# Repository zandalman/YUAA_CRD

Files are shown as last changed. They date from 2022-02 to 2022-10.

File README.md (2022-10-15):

## YUAA CRD

### Purpose
Our goal is to develop a cosmic ray detector (CRD) to serve as the scientific payload for the Yale Undergraduate Aerospace Association (YUAA) CubeSat. We will use cosmic rays to map the boundaries of the South Atlantic Anomaly (SAA).

### General CubeSat Info

CubeSats are miniature satellites composed of units consisting of 10 cm cubes. Yale was chosen by NASA as one of sixteen schools across the country whose CubeSat will be launched into space as auxiliary payloads on NASA missions. The Yale CubeSat consists of two 10 cm cube units. The CubeSat team is divided into several subteams: attitude determination and control (ADCS), radio, software, and cosmic ray detector (CRD). The CRD team interacts significantly with the ADCS and software teams. The software team writes C programs for our I2C components. We work with the ADCS team to coordinate mechanical design in the CubeSat, which is necessary due to the size constraints. The bulkiest part of the ADCS system is the gravity gradient boom (GGB), a measuring tape which spools out of the bottom of the CubeSat to generate restoring torques which stabilize the CubeSat’s orientation. The GGB includes a rotary encoder which provides feedback on the length of the GGB. The ADCS system also includes magnetorquers, electromagnets which generate torques using the Earth’s magnetic field, to maneuver the CubeSat.

### Background

#### Cosmic Rays

Cosmic rays are high-energy radiation originating from outside the solar system. About 99% of cosmic rays are bare atomic nuclei. 90% of these nuclei are protons (hydrogen nuclei), 9% are alpha particles (helium nuclei), and 1% are heavier elements. The other 1% of cosmic rays are beta particles (solitary electrons). Cosmic rays also include trace amounts of antiparticles like positrons and antiprotons. Sometimes, gamma rays (high-energy photons) are also considered cosmic rays. When cosmic rays enter the Earth’s atmosphere, they collide with atoms and molecules, producing a cascade of lighter particles known as secondary cosmic rays. Secondary cosmic rays are typically composed of neutrons, pions, kaons, and their antiparticles. Pions and kaons quickly decay into muons, neutrinos, and their antiparticles, which can be detected on Earth’s surface. The muon lifetime of 2.2 us should not be enough for muons to reach the surface of Earth, but due to relativistic time dilation their effective lifetime is longer in our reference frame. 1 Muons have similar properties to electrons but about 200 times the mass. Because muons are charged particles, we can use muons to test our detection circuitry before sending it into space.

#### Earth’s Magnetic Field

The Earth has a dipolar magnetic field generated by convection currents in Earth’s molten iron and nickel outer core. Energetic charged particles originating from solar wind and cosmic rays are captured by Earth’s magnetic field. Charged particles in a magnetic field move in helices about magnetic field lines. The concentration of charged particles peaks in two distinct regions above Earth’s surface, known as the inner and outer Van Allen belts. The gap between the Van Allen belts is caused by low frequency radio waves whose origin is still an area of active
research. 

There is a nonzero angle between the axis of Earth’s dipole magnetic field and its axis of rotation, causing the inner Van Allen belt to make its closest approach of about 2000 km to Earth’s surface above the South Atlantic. This region of enhanced radiation is called the South Atlantic Anomaly (SAA). The SAA dips low enough to intersect low Earth orbit. Satellites passing through the SAA are exposed to elevated levels of radiation for minutes at a time, leading to malfunctions, loss of observational time for telescopes, and danger to astronauts in the ISS.

#### Scintillators

A scintillator is a material that emits photons when excited by ionizing radiation. Commonly used scintillators often emit photons in the optical bands. There are many types of scintillators including organic crystals, organic liquids, plastic scintillators, inorganic crystals, gaseous scintillators, glasses, and perovskites. We use plastic scintillators, in which the primary fluorescent emitter, or fluor, is suspended in a base.

### Design

#### Mechanical

Using a band saw and a mill, we cut the scintillator down to a 1 cm cube due to size constraints in the CubeSat. Within the SAA, the particle flux is so high that our detection events would overlap. A layer of aluminum shielding around the scintillator reduces the number of events to the order of ~100 events per second. We calculated that a shielding thickness of 7 mm is sufficient. Because protons are more massive than electrons, cosmic ray protons typically have more energy than cosmic ray electrons, so the ratio of proton to electron events increases with shielding thickness.

The shielding is a 25 x 25 x 28 mm rectangular prism of aluminum with an 11 x 11 x 14 mm hole in the center for the scintillator cube and the SiPM. For ease of machining, the shielding is composed of 3 sections which are held together by 6-32 screws. At each of the bottom corners, the aluminum extends slightly further to give space for mounting holes.

When a charged particle passes through the scintillator, it deposits its kinetic energy into photons. We coat five sides of the scintillator with a reflective paint so that most photons eventually exit the scintillator at a single face. The non-coated face has a silicon photomultiplier (SiPM) which will detect the photons. The SiPM is optically coupled to the scintillator with optical jelly, an amorphous material with a prescribed refractive index. The SiPM is held fast against the scintillator by rubber stops which push against the inside faces of the shielding.

The SiPM is soldered onto a small printed circuit board (PCB) using a ball grid array (BGA). The PCB contains pads for the anode and cathode. Wires will be soldered directly to these pads and exit the shielding through a hole. The SiPM is AC coupled to a charge-sensitive preamplifier (preamp). The AC coupling circuit and the preamp come from an evaluation kit created by Ketek. The AC coupling circuit is mounted in a Thorlabs mount and the preamp is mounted in a rectangular aluminum box which acts as a Faraday cage, protecting it from radiation.

All of the circuitry minus the AC coupling circuit and preamp are contained on a custom 4-layer PCB, whose irregular shape is determined by the size constraints imposed by the GGB. This custom PCB will connect to the SiPM, AC coupling circuit, and preamp by a combination of wires and micro coax cables. Wires will be twisted together in pairs for extra stability.

#### Electrical

Our custom analog circuitry will count the number of cosmic ray detection events and classify them according to particle type. Our integrated circuit (IC) components communicate with the onboard computer (OBC) using I2C protocol, which requires clock and data lines. We have access to one set of clock and data lines from the OBC. An important aspect of I2C is that two devices cannot use the same clock and data lines if they have the same I2C address. Most IC chips which use I2C have address pins which allow you to set the I2C address to avoid overlap. We also have access to a 5 V power supply from the OBC.

As charged particles pass through the scintillator, their kinetic energy is converted into photons which activate cells on the SiPM. The SiPM is an avalanche photodiode, meaning that it consists of an array of photodiode cells. When a photon hits a cell, the cell emits electrons via the photoelectric effect. There is some “dead time” where the cell cannot detect another photon, so having an array of cells allows the SiPM to detect many photons in quick succession. The output pulse generated by the SiPM from a detection event is a sum of the signals generated by all of the photons produced by the particle passing through the scintillator.

The SiPM is AC coupled to a charge-sensitive preamp. In contrast to DC coupling, AC coupling rejects DC components of the signal, blocking any DC bias or offset voltage. AC coupling becomes important when the pulse frequency is sufficiently high that pulses overlap, resulting in a nonzero offset.

The preamp creates output pulses with an integrated voltage equal to the integrated current (i.e. charge) of the input pulses. The charge of the input pulses is physically meaningful because it is proportional to the total energy of the photons collected by the SiPM. The output pulses from the pre-amp look like a steep rising edge followed by an exponential decay with a time constant of ~100 ns. The height of the pulses ranges from 10 mV to 100 mV depending on the type of particle. Because all pulses have approximately the same shape, we can use the height of the pulse as a proxy for the integrated voltage. This pulse height analysis (PHA) is common in radiation detection.

If we had a larger budget, we would use a commercial multi-channel analyzer (MCA). However, instead we bin pulses by pulse height manually. Each pulse height bin is created with a system of three high-speed comparators. Two comparators act as upper and lower discriminators and a third comparator acts as an AND gate, only outputting high if the input voltage is between the two discriminators. The comparators are contained in IC chips with 4 comparators each. We have 7 bins total, so we need 21 comparators or 6 IC chips. The discriminator levels are set by 8 bit digital-to-analog converters (DACs). The DACs are contained in an IC chip with 8 DACs.

The outputs from the comparators are fed into real time clock (RTC) IC chips, which we program to count the number of pulses over the course of 5 min. There are 8 RTC chips, 7 for the pulse height bins and one for counting pulses from the rotary encoder for the GGB. The RTC chips only have one I2C address bin and therefore only two possible I2C addresses. We use an I2C multiplexer to mediate communication between the OBC and the RTC chips. The multiplexer has one input set of clock and data lines and four output sets of clock and data lines which each are used by 2 RTC chips, one with each possible I2C address.

We only have access to a 5 V power supply from the OBC. However, the preamp requires a 12 V power supply and the AC coupling circuit requires a 30 V bias voltage. We use boost converters to generate these voltages from the 5 V supply. All components draw negligible current, so there is no worry about drawing too much current.

The light output of the scintillator is temperature dependent and we don’t know exactly what the equilibrium temperature will be in the CubeSat once it is in space. Therefore, we use resistor temperature devices (RTDs) to monitor the temperature on our custom PCB and near the shielding.

The code for interfacing between the OBC and the I2C components of the circuit is managed by
the software subteam of the CubeSat and is available upon request.

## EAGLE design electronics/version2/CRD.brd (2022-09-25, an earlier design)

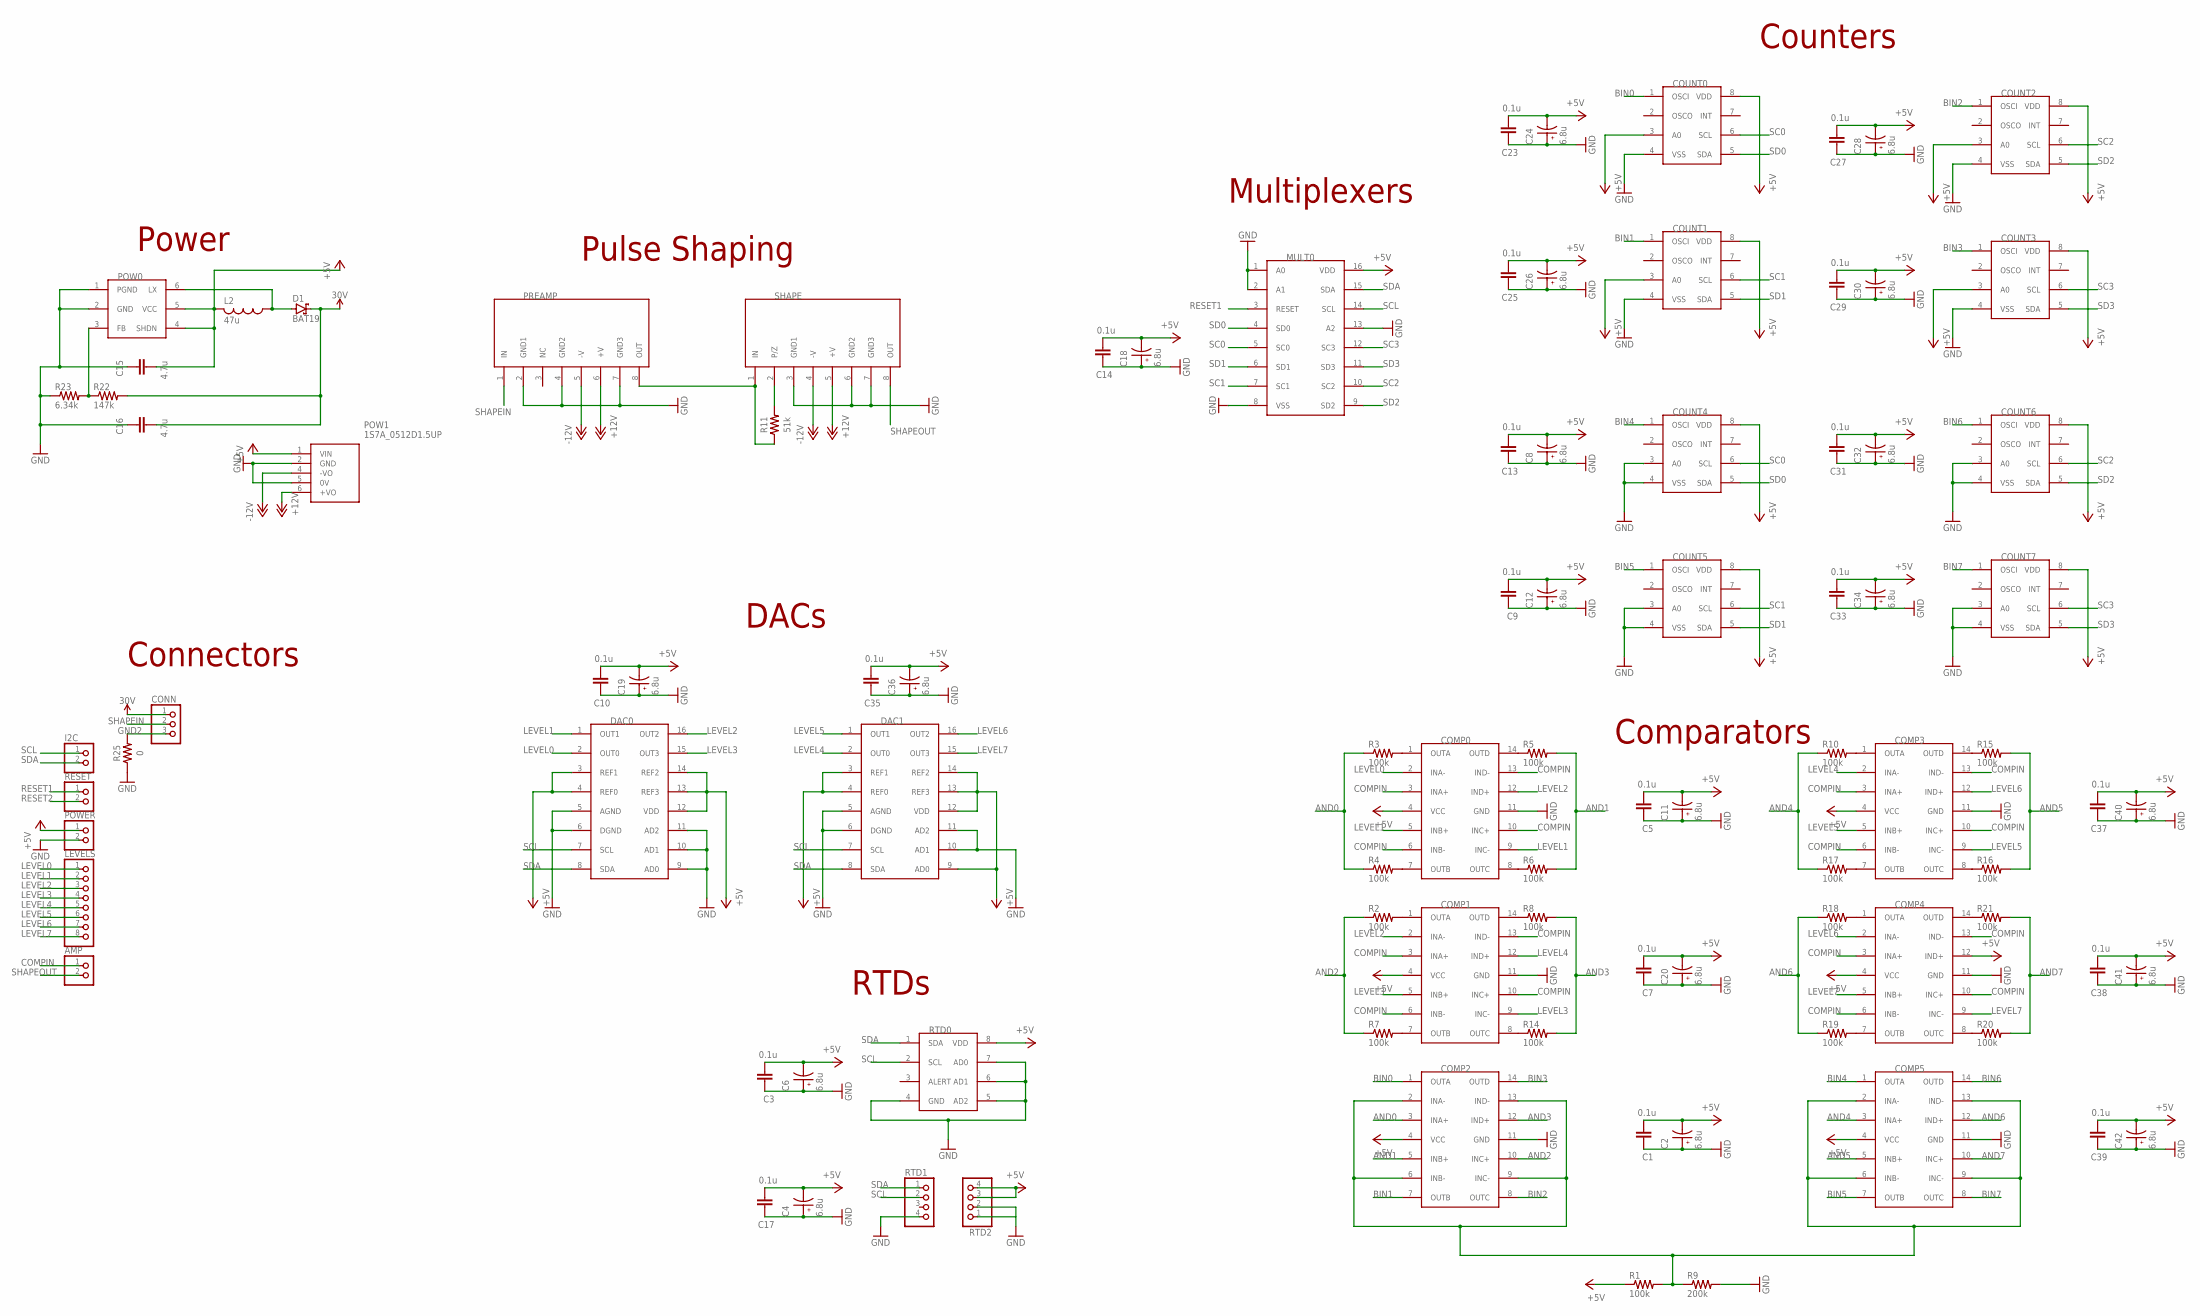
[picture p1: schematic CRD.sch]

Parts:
AMP: PINHD-1X2; 1X02
C1, C3, C5, C7, C9, C10, C13, C14, C17, C23, C25, C27, C29, C31, C33, C35, C37, C38, C39: 0.1u; CAP_1206
C2, C4, C6, C8, C11, C12, C18, C19, C20, C24, C26, C28, C30, C32, C34, C36, C40, C41, C42: 6.8u; CAPPRD150W45D400H700
C15, C16: 4.7u; CAP_1206
COMP0, COMP1, COMP2, COMP3, COMP4, COMP5: MAX9108ESD+; SOIC127P600X155-14N
CONN: PINHD-1X3; 1X03
COUNT0, COUNT1, COUNT2, COUNT3, COUNT4, COUNT5, COUNT6, COUNT7: PCF8583; SOIC127P1032X265-8N
D1: BAT19; DO35-10
DAC0, DAC1: MAX520BEWE+; SOIC127P1032X265-16N
I2C: PINHD-1X2; 1X02
L2: 47u; L1812
LEVELS: PINHD-1X8; 1X08
MULT0: PCA9546A; SOIC127P600X175-16N
POW0: MAX5025; SOT95P240X110-6N
POW1: 1S7A_0512D1.5UP; 1S7A_0505D15UP
POWER: PINHD-1X2; 1X02
PREAMP: CR-113; HDRV8W64P254_1X8_1016X508X838B
R1, R2, R3, R4, R5, R6, R7, R8, R10, R14, R15, R16, R17, R18, R19, R20, R21: 100k; RES_1206
R9: 200k; RES_1206
R11: 51k; RESAD1176W63L850D250B
R22: 147k; RES_1206
R23: 6.34k; RES_1206
R25: 0; RESAD724W46L381D178B
RESET: PINHD-1X2; 1X02
RTD0: NCT175DMR2G; SOP65P490X110-8N
RTD1, RTD2: PINHD-1X4; 1X04
SHAPE: CR-200; HDRV8W64P254_1X8_1016X508X838B

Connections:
+5V: C1.2, C2.N, C3.2, C4.N, C5.2, C6.N, C7.2, C8.N, C9.2, C10.2, C11.N, C12.N, C13.2, C14.2, C15.2, C17.2, C18.N, C19.N, C20.N, C23.2, C24.N, C25.2, C26.N, C27.2, C28.N, C29.2, C30.N, C31.2, C32.N, C33.2, C34.N, C35.2, C36.N, C37.2, C38.2, C39.2, C40.N, C41.N, C42.N, COMP0.4 (VCC), COMP1.4 (VCC), COMP2.4 (VCC), COMP3.4 (VCC), COMP4.4 (VCC), COMP4.12 (IND+), COMP5.4 (VCC), COUNT0.3 (A0), COUNT0.8 (VDD), COUNT1.3 (A0), COUNT1.8 (VDD), COUNT2.3 (A0), COUNT2.8 (VDD), COUNT3.3 (A0), COUNT3.8 (VDD), COUNT4.8 (VDD), COUNT5.8 (VDD), COUNT6.8 (VDD), COUNT7.8 (VDD), DAC0.3 (REF1), DAC0.4 (REF0), DAC0.12 (VDD), DAC0.13 (REF3), DAC0.14 (REF2), DAC1.3 (REF1), DAC1.4 (REF0), DAC1.9 (AD0), DAC1.12 (VDD), DAC1.13 (REF3), DAC1.14 (REF2), L2.2, MULT0.16 (VDD), POW0.4 (SHDN), POW0.5 (VCC), POW1.1 (VIN), POWER.1, R1.1, RTD0.8 (VDD), RTD2.3, RTD2.4
+12V: POW1.6 (+VO), PREAMP.6 (+V), SHAPE.5 (+V)
-12V: POW1.4 (-VO), PREAMP.5 (-V), SHAPE.4 (-V)
AND0: COMP2.3 (INA+), R3.1, R4.1
AND1: COMP2.5 (INB+), R5.2, R6.2
AND2: COMP2.10 (INC+), R2.1, R7.1
AND3: COMP2.12 (IND+), R8.2, R14.2
AND4: COMP5.3 (INA+), R10.1, R17.1
AND5: COMP5.5 (INB+), R15.2, R16.2
AND6: COMP5.12 (IND+), R18.1, R19.1
AND7: COMP5.10 (INC+), R20.2, R21.2
BIN0: COMP2.1 (OUTA), COUNT0.1 (OSCI)
BIN1: COMP2.7 (OUTB), COUNT1.1 (OSCI)
BIN2: COMP2.8 (OUTC), COUNT2.1 (OSCI)
BIN3: COMP2.14 (OUTD), COUNT3.1 (OSCI)
BIN4: COMP5.1 (OUTA), COUNT4.1 (OSCI)
BIN5: COMP5.7 (OUTB), COUNT5.1 (OSCI)
BIN6: COMP5.14 (OUTD), COUNT6.1 (OSCI)
BIN7: COMP5.8 (OUTC), COUNT7.1 (OSCI)
COMPIN: AMP.1, COMP0.3 (INA+), COMP0.6 (INB-), COMP0.10 (INC+), COMP0.13 (IND-), COMP1.3 (INA+), COMP1.6 (INB-), COMP1.10 (INC+), COMP1.13 (IND-), COMP3.3 (INA+), COMP3.6 (INB-), COMP3.10 (INC+), COMP3.13 (IND-), COMP4.3 (INA+), COMP4.6 (INB-), COMP4.10 (INC+), COMP4.13 (IND-)
GND: C1.1, C2.P, C3.1, C4.P, C5.1, C6.P, C7.1, C8.P, C9.1, C10.1, C11.P, C12.P, C13.1, C14.1, C15.1, C16.1, C17.1, C18.P, C19.P, C20.P, C23.1, C24.P, C25.1, C26.P, C27.1, C28.P, C29.1, C30.P, C31.1, C32.P, C33.1, C34.P, C35.1, C36.P, C37.1, C38.1, C39.1, C40.P, C41.P, C42.P, COMP0.11 (GND), COMP1.11 (GND), COMP2.11 (GND), COMP3.11 (GND), COMP4.11 (GND), COMP5.11 (GND), COUNT0.4 (VSS), COUNT1.4 (VSS), COUNT2.4 (VSS), COUNT3.4 (VSS), COUNT4.3 (A0), COUNT4.4 (VSS), COUNT5.3 (A0), COUNT5.4 (VSS), COUNT6.3 (A0), COUNT6.4 (VSS), COUNT7.3 (A0), COUNT7.4 (VSS), DAC0.5 (AGND), DAC0.6 (DGND), DAC0.9 (AD0), DAC0.10 (AD1), DAC0.11 (AD2), DAC1.5 (AGND), DAC1.6 (DGND), DAC1.10 (AD1), DAC1.11 (AD2), MULT0.1 (A0), MULT0.2 (A1), MULT0.8 (VSS), MULT0.13 (A2), POW0.1 (PGND), POW0.2 (GND), POW1.2 (GND), POW1.5 (0V), POWER.2, PREAMP.2 (GND1), PREAMP.4 (GND2), PREAMP.7 (GND3), R9.2, R23.1, R25.1, RTD0.4 (GND), RTD0.5 (AD2), RTD0.6 (AD1), RTD0.7 (AD0), RTD1.4, RTD2.2, SHAPE.3 (GND1), SHAPE.6 (GND2), SHAPE.7 (GND3)
GND2: CONN.3, R25.2
LEVEL0: COMP0.2 (INA-), DAC0.2 (OUT0), LEVELS.1
LEVEL1: COMP0.5 (INB+), COMP0.9 (INC-), DAC0.1 (OUT1), LEVELS.2
LEVEL2: COMP0.12 (IND+), COMP1.2 (INA-), DAC0.16 (OUT2), LEVELS.3
LEVEL3: COMP1.5 (INB+), COMP1.9 (INC-), DAC0.15 (OUT3), LEVELS.4
LEVEL4: COMP1.12 (IND+), COMP3.2 (INA-), DAC1.2 (OUT0), LEVELS.5
LEVEL5: COMP3.5 (INB+), COMP3.9 (INC-), DAC1.1 (OUT1), LEVELS.6
LEVEL6: COMP3.12 (IND+), COMP4.2 (INA-), DAC1.16 (OUT2), LEVELS.7
LEVEL7: COMP4.5 (INB+), COMP4.9 (INC-), DAC1.15 (OUT3), LEVELS.8
unnamed: COMP0.1 (OUTA), R3.2
unnamed: COMP0.7 (OUTB), R4.2
unnamed: COMP0.14 (OUTD), R5.1
unnamed: COMP0.8 (OUTC), R6.1
unnamed: COMP1.1 (OUTA), R2.2
unnamed: COMP1.7 (OUTB), R7.2
unnamed: COMP1.14 (OUTD), R8.1
unnamed: COMP1.8 (OUTC), R14.1
unnamed: PREAMP.8 (OUT), R11.1, SHAPE.1 (IN)
unnamed: R11.2, SHAPE.2 (P/Z)
unnamed: D1.A, L2.1, POW0.6 (LX)
unnamed: POW0.3 (FB), R22.1, R23.2
unnamed: COMP2.2 (INA-), COMP2.6 (INB-), COMP2.9 (INC-), COMP2.13 (IND-), COMP5.2 (INA-), COMP5.6 (INB-), COMP5.9 (INC-), COMP5.13 (IND-), R1.2, R9.1
unnamed: COMP3.1 (OUTA), R10.2
unnamed: COMP3.14 (OUTD), R15.1
unnamed: COMP3.8 (OUTC), R16.1
unnamed: COMP3.7 (OUTB), R17.2
unnamed: COMP4.1 (OUTA), R18.2
unnamed: COMP4.7 (OUTB), R19.2
unnamed: COMP4.8 (OUTC), R20.1
unnamed: COMP4.14 (OUTD), R21.1
RESET1: MULT0.3 (RESET), RESET.1
RESET2: RESET.2
SC0: COUNT0.6 (SCL), COUNT4.6 (SCL), MULT0.5 (SC0)
SC1: COUNT1.6 (SCL), COUNT5.6 (SCL), MULT0.7 (SC1)
SC2: COUNT2.6 (SCL), COUNT6.6 (SCL), MULT0.10 (SC2)
SC3: COUNT3.6 (SCL), COUNT7.6 (SCL), MULT0.12 (SC3)
SCL: DAC0.7 (SCL), DAC1.7 (SCL), I2C.1, MULT0.14 (SCL), RTD0.2 (SCL), RTD1.2
SD0: COUNT0.5 (SDA), COUNT4.5 (SDA), MULT0.4 (SD0)
SD1: COUNT1.5 (SDA), COUNT5.5 (SDA), MULT0.6 (SD1)
SD2: COUNT2.5 (SDA), COUNT6.5 (SDA), MULT0.9 (SD2)
SD3: COUNT3.5 (SDA), COUNT7.5 (SDA), MULT0.11 (SD3)
SDA: DAC0.8 (SDA), DAC1.8 (SDA), I2C.2, MULT0.15 (SDA), RTD0.1 (SDA), RTD1.1
SHAPEIN: CONN.2, PREAMP.1 (IN)
SHAPEOUT: AMP.2, SHAPE.8 (OUT)
VIN: C16.2, CONN.1, D1.C, R22.2

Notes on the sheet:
Power
Pulse Shaping
Connectors
Counters
RTDs
Multiplexers
DACs
Comparators

Board: 2 copper layers, 94 parts (0 on the bottom side), 65 nets, no tracks yet.

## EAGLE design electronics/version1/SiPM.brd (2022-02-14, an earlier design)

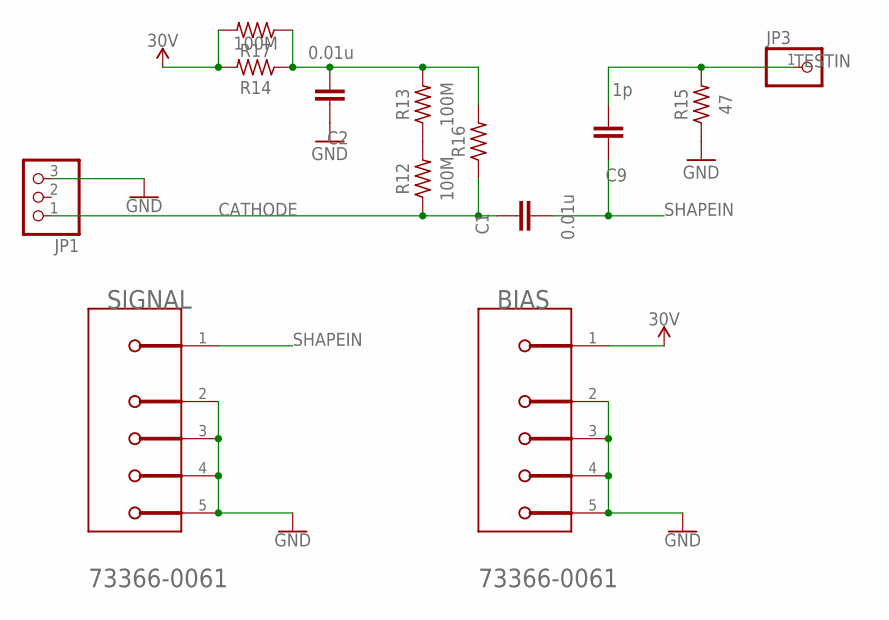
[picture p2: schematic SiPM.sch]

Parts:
BIAS: MOLEX_73366-0061MOLEX_73366-0061_0_0; MOLEX_73366-0061_0
C1, C2: 0.01u; CAP_1206
C9: 1p; CAP_1206
JP1: PINHD-1X3; 1X03
JP3: PINHD-1X1; 1X01
R12, R13, R14: 100M; RESAD1176W63L850D250B
R15: 47; RESAD1176W63L850D250B
R16, R17: R-US_AXIAL-11.7MM-PITCH; RESAD1176W63L850D250B
SIGNAL: MOLEX_73366-0061MOLEX_73366-0061_0_0; MOLEX_73366-0061_0

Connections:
CATHODE: C1.1, JP1.1, R12.1, R16.1
GND: BIAS.2 (MNT_1), BIAS.3 (MNT_2), BIAS.4 (MNT_3), BIAS.5 (MNT_4), C2.1, JP1.3, R15.1, SIGNAL.2 (MNT_1), SIGNAL.3 (MNT_2), SIGNAL.4 (MNT_3), SIGNAL.5 (MNT_4)
unnamed: R12.2, R13.1
unnamed: C2.2, R13.2, R14.1, R16.2, R17.1
SHAPEIN: C1.2, C9.1, SIGNAL.1
TESTIN: C9.2, JP3.1, R15.2
VIN: BIAS.1, R14.2, R17.2

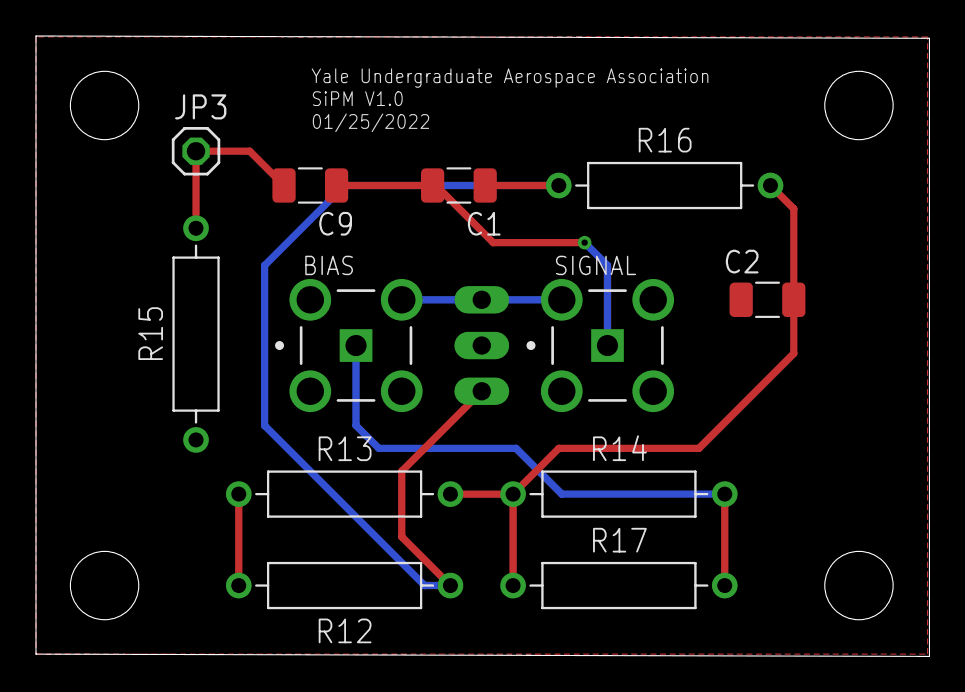
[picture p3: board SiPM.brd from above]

Board: 2 copper layers, 49.6 x 34.5 mm, 13 parts (1 on the bottom side), 7 nets.

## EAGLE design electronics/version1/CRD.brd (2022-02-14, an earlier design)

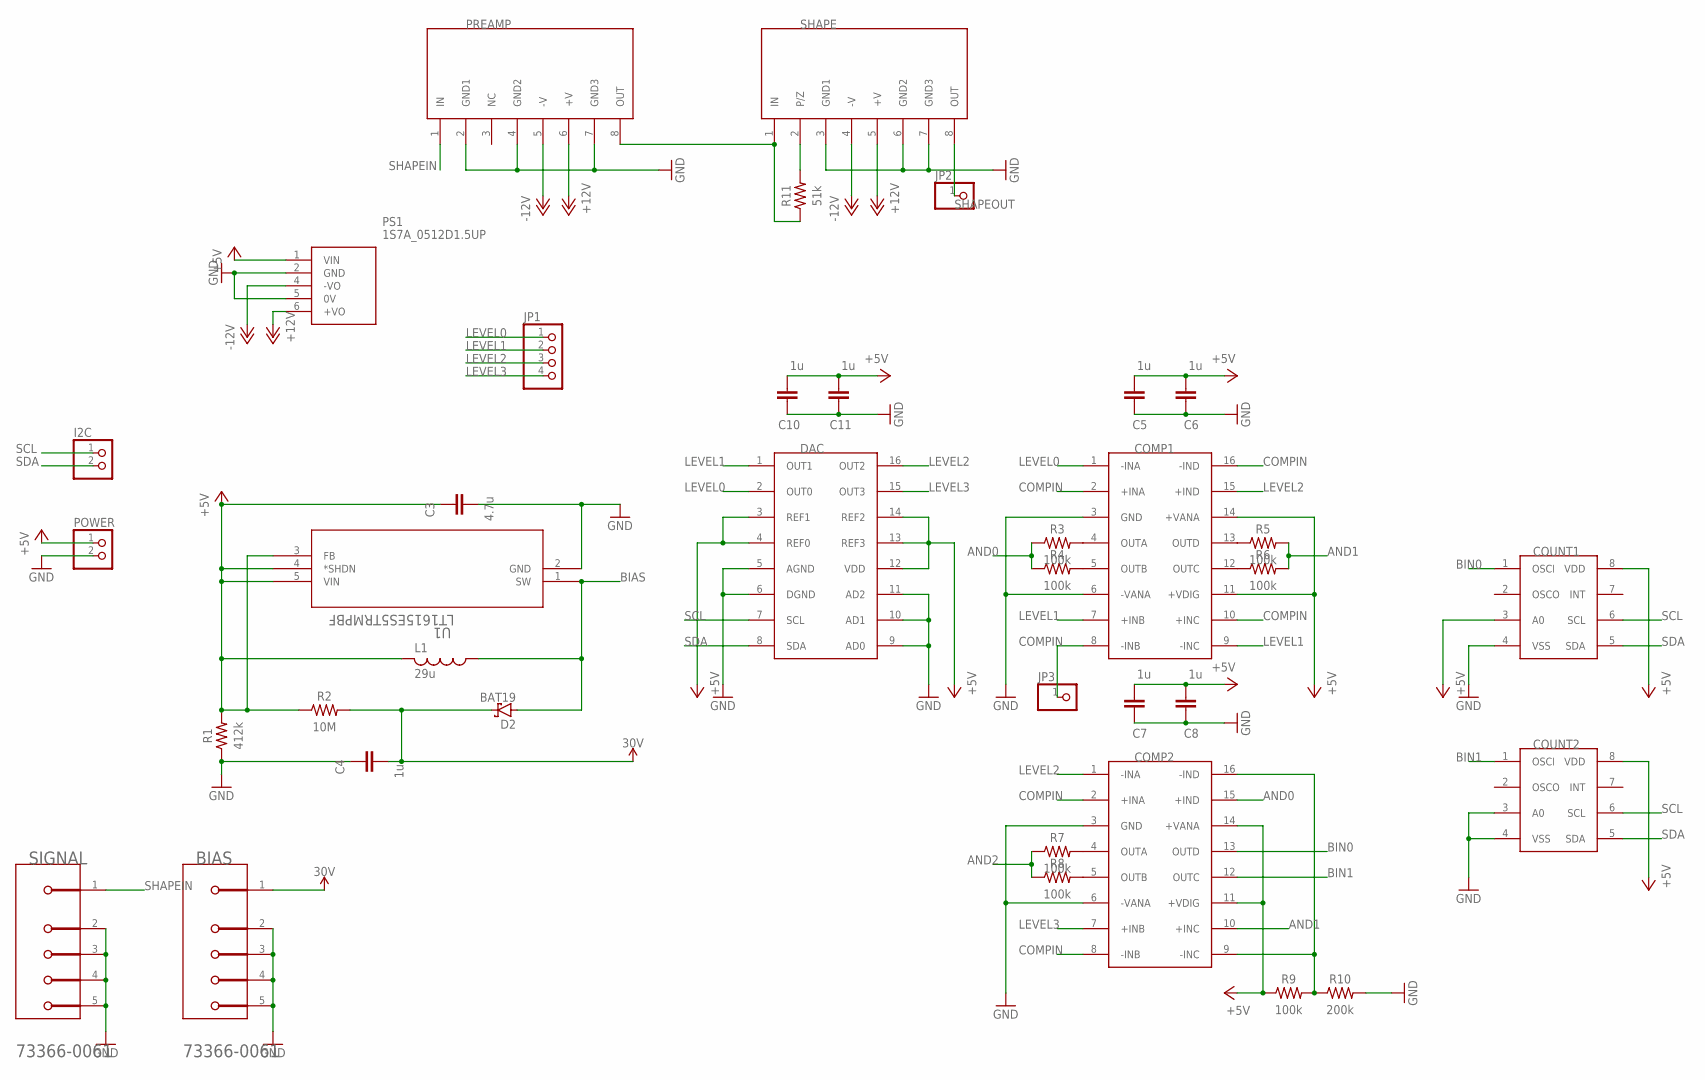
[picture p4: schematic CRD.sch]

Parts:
BIAS: MOLEX_73366-0061MOLEX_73366-0061_0_0; MOLEX_73366-0061_0
C3: 4.7u; CAP_1206
C4, C5, C6, C7, C8, C10, C11: 1u; CAP_1206
COMP1, COMP2: AD8564ARZ; SOIC127P1032X265-16N
COUNT1, COUNT2: PCF8583; SOIC127P1032X265-8N
D2: BAT19; DO35-10
DAC: MAX520BEWE+; SOIC127P1032X265-16N
I2C: PINHD-1X2; 1X02
JP1: PINHD-1X4; 1X04
JP2, JP3: PINHD-1X1; 1X01
L1: 29u; L1812
POWER: PINHD-1X2; 1X02
PREAMP: CR-113; HDRV8W64P254_1X8_1016X508X838B
PS1: 1S7A_0512D1.5UP; 1S7A_0505D15UP
R1: 412k; RESAD1176W63L850D250B
R2: 10M; RESAD1176W63L850D250B
R3, R4, R5, R6, R7, R8, R9: 100k; RESAD1176W63L850D250B
R10: 200k; RESAD1176W63L850D250B
R11: 51k; RESAD1176W63L850D250B
SHAPE: CR-200; HDRV8W64P254_1X8_1016X508X838B
SIGNAL: MOLEX_73366-0061MOLEX_73366-0061_0_0; MOLEX_73366-0061_0
U1: LT1615ES5TRMPBF; SOT-5_S

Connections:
+5V: C3.1, C5.2, C6.2, C7.2, C8.2, C10.2, C11.2, COMP1.11 (+VDIG), COMP1.14 (+VANA), COMP2.11 (+VDIG), COMP2.14 (+VANA), COUNT1.3 (A0), COUNT1.8 (VDD), COUNT2.8 (VDD), DAC.3 (REF1), DAC.4 (REF0), DAC.12 (VDD), DAC.13 (REF3), DAC.14 (REF2), L1.2, POWER.1, PS1.1 (VIN), R1.2, R2.1, R9.1, U1.3 (FB), U1.4 (*SHDN), U1.5 (VIN)
+12V: PREAMP.6 (+V), PS1.6 (+VO), SHAPE.5 (+V)
-12V: PREAMP.5 (-V), PS1.4 (-VO), SHAPE.4 (-V)
AND0: COMP2.15 (+IND), R3.1, R4.1
AND1: COMP2.10 (+INC), R5.2, R6.2
AND2: R7.1, R8.1
BIAS: D2.A, L1.1, U1.1 (SW)
BIN0: COMP2.13 (OUTD), COUNT1.1 (OSCI)
BIN1: COMP2.12 (OUTC), COUNT2.1 (OSCI)
COMPIN: COMP1.2 (+INA), COMP1.8 (-INB), COMP1.10 (+INC), COMP1.16 (-IND), COMP2.2 (+INA), COMP2.8 (-INB), JP3.1
GND: BIAS.2 (MNT_1), BIAS.3 (MNT_2), BIAS.4 (MNT_3), BIAS.5 (MNT_4), C3.2, C4.1, C5.1, C6.1, C7.1, C8.1, C10.1, C11.1, COMP1.3 (GND), COMP1.6 (-VANA), COMP2.3 (GND), COMP2.6 (-VANA), COUNT1.4 (VSS), COUNT2.3 (A0), COUNT2.4 (VSS), DAC.5 (AGND), DAC.6 (DGND), DAC.9 (AD0), DAC.10 (AD1), DAC.11 (AD2), POWER.2, PREAMP.2 (GND1), PREAMP.4 (GND2), PREAMP.7 (GND3), PS1.2 (GND), PS1.5 (0V), R1.1, R10.2, SHAPE.3 (GND1), SHAPE.6 (GND2), SHAPE.7 (GND3), SIGNAL.2 (MNT_1), SIGNAL.3 (MNT_2), SIGNAL.4 (MNT_3), SIGNAL.5 (MNT_4), U1.2 (GND)
LEVEL0: COMP1.1 (-INA), DAC.2 (OUT0), JP1.1
LEVEL1: COMP1.7 (+INB), COMP1.9 (-INC), DAC.1 (OUT1), JP1.2
LEVEL2: COMP1.15 (+IND), COMP2.1 (-INA), DAC.16 (OUT2), JP1.3
LEVEL3: COMP2.7 (+INB), DAC.15 (OUT3), JP1.4
unnamed: COMP1.4 (OUTA), R3.2
unnamed: COMP1.5 (OUTB), R4.2
unnamed: COMP1.13 (OUTD), R5.1
unnamed: COMP1.12 (OUTC), R6.1
unnamed: COMP2.4 (OUTA), R7.2
unnamed: COMP2.5 (OUTB), R8.2
unnamed: PREAMP.8 (OUT), R11.1, SHAPE.1 (IN)
unnamed: R11.2, SHAPE.2 (P/Z)
unnamed: COMP2.9 (-INC), COMP2.16 (-IND), R9.2, R10.1
SCL: COUNT1.6 (SCL), COUNT2.6 (SCL), DAC.7 (SCL), I2C.1
SDA: COUNT1.5 (SDA), COUNT2.5 (SDA), DAC.8 (SDA), I2C.2
SHAPEIN: PREAMP.1 (IN), SIGNAL.1
SHAPEOUT: JP2.1, SHAPE.8 (OUT)
VIN: BIAS.1, C4.2, D2.C, R2.2

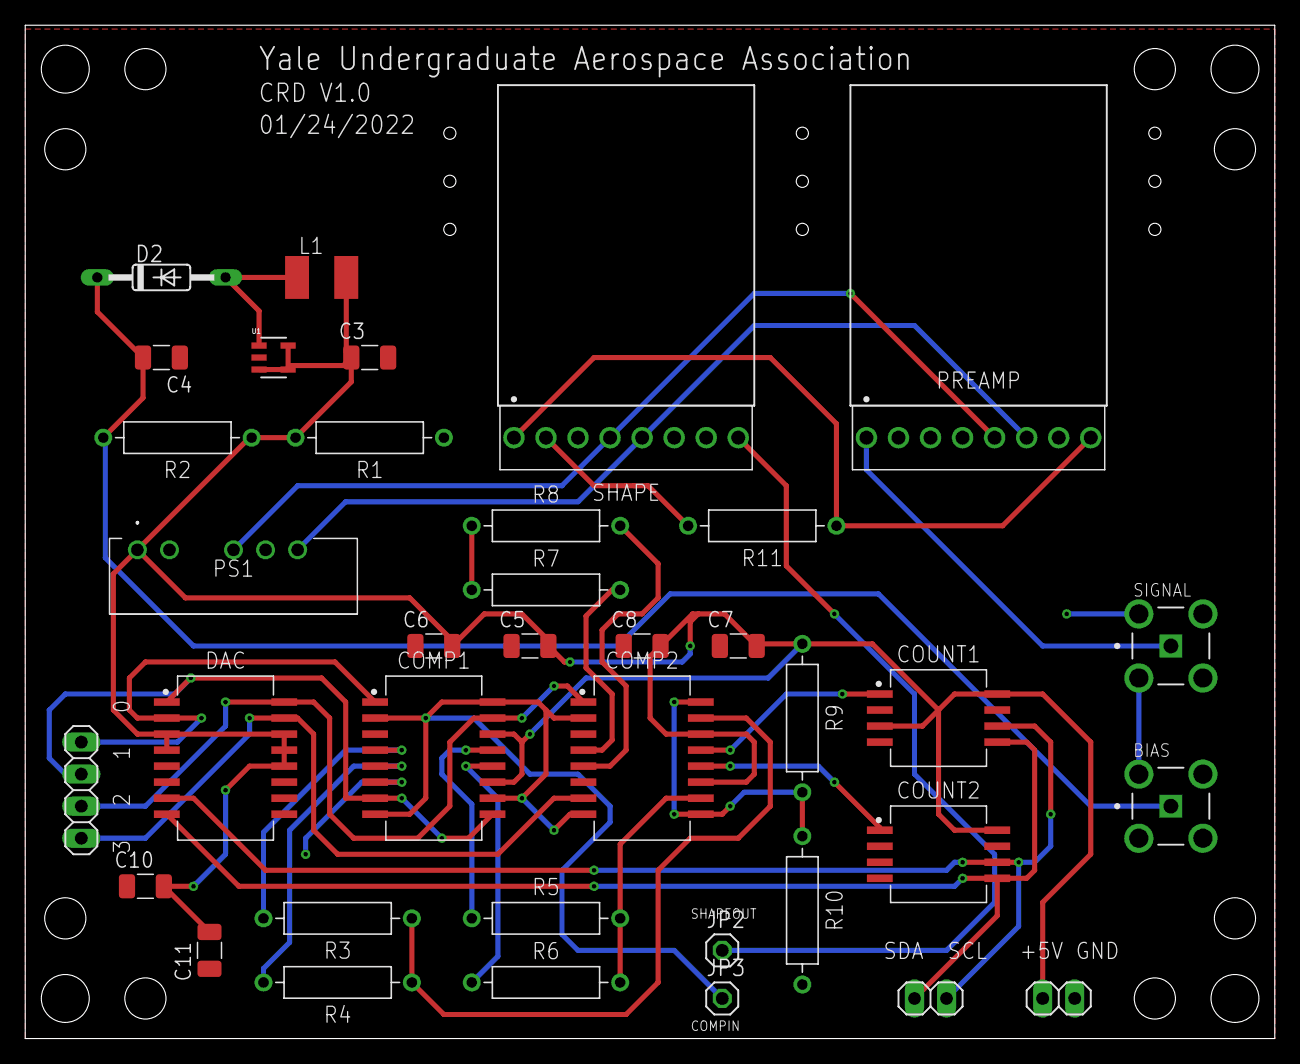
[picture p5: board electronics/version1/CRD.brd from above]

Board: 2 copper layers, 99.0 x 80.3 mm, 37 parts (0 on the bottom side), 29 nets.

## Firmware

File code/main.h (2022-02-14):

/*!
*~~~~~~~~~~~~~~~~~~~~~~~~~~~~~~~~~~~~~~~~~~~~~~~~~~~~~~~~~~~~~~~~~~~~~~~~~~~~~~~~~~~~~~~~~~~
* @file main.h
* @brief Header of main.c
*~~~~~~~~~~~~~~~~~~~~~~~~~~~~~~~~~~~~~~~~~~~~~~~~~~~~~~~~~~~~~~~~~~~~~~~~~~~~~~~~~~~~~~~~~~~
* @author            Vasil Milev
* @version           1.0.0
* @date              2018.07.04
*
* @copyright         (C) Copyright Endurosat
*
*                    Contents and presentations are protected world-wide.
*                    Any kind of using, copying etc. is prohibited without prior permission.
*                    All rights - incl. industrial property rights - are reserved.
*
* @history
* @revision{         1.0.0  , 2018.07.04, author Vasil Milev, Initial revision }
* @endhistory
*~~~~~~~~~~~~~~~~~~~~~~~~~~~~~~~~~~~~~~~~~~~~~~~~~~~~~~~~~~~~~~~~~~~~~~~~~~~~~~~~~~~~~~~~~~~
*/
#ifndef MAIN_H
#define MAIN_H

/*
*~~~~~~~~~~~~~~~~~~~~~~~~~~~~~~~~~~~~~~~~~~~~~~~~~~~~~~~~~~~~~~~~~~~~~~~~~~~~~~~~~~~~~~~~~~~
* INCLUDES
*~~~~~~~~~~~~~~~~~~~~~~~~~~~~~~~~~~~~~~~~~~~~~~~~~~~~~~~~~~~~~~~~~~~~~~~~~~~~~~~~~~~~~~~~~~~
*/
#include "stm32f4xx_hal.h"
#include <stdio.h>

/*
*~~~~~~~~~~~~~~~~~~~~~~~~~~~~~~~~~~~~~~~~~~~~~~~~~~~~~~~~~~~~~~~~~~~~~~~~~~~~~~~~~~~~~~~~~~~
* EXTERNAL DEFINES
*~~~~~~~~~~~~~~~~~~~~~~~~~~~~~~~~~~~~~~~~~~~~~~~~~~~~~~~~~~~~~~~~~~~~~~~~~~~~~~~~~~~~~~~~~~~
*/

#if !defined(__FILE_defined)
//typedef __FILE FILE;
# define __FILE_defined
#endif

/* USARTs related definitions */
#define UART_BUFFER_SIZE    256
#define LINE_BUFFER_SIZE UART_BUFFER_SIZE
/* End of USARTs related definitions */

/* LED related definitions */
#define GREEN_LED_ON() GPIOC->ODR |= 0x0010;
#define GREEN_LED_OFF() GPIOC->ODR &= ~0x0010;
#define GREEN_LED_XOR() GPIOC->ODR ^= 0x0010;
#define AMBER_LED_ON() GPIOC->ODR |= 0x0020;
#define AMBER_LED_OFF() GPIOC->ODR &= ~0x0020;
#define AMBER_LED_XOR() GPIOC->ODR ^= 0x0020;
/* End of LED related definitions */

/* ESTTC related definitions */
#define EPS_I2C_ADDRESS         0x18
#define EPS_OUT_PAR_NUM         19
#define EPS_MAX_PAR_NUM         (48+1)
#define ANT_I2C_ADDRESS         0x33
#define UHF_I2C_ADDRESS         0x22
#define UHF_MAX_PAR_NUM         8
#define OBC_I2C_ADDRESS         0x11
#define S_X_BAND_ADDRESS        0x40
/* End of ESTTC related definitions */

/* Bootloader related definitions */
#define APPL_ADDRESS            0x08040000
#define BOOT_ADDRESS            0x08000000
#define RTC_INIT_ADDRESS        0x40002850
#define MAILBOX_ADDRESS         0x40002854
#define MAILBOX_VAL_BOOT        0xB007B007
#define MAILBOX_VAL_APPL        0xA552A552
#define MAILBOX_VAL_HARD        0x0BAD0BAD

#define FLASH_BLANK             0xFF
#define FLASH_SECTOR_SIZE       0x20000
#define FLASH_MIN_SECTOR        6
#define FLASH_MAX_SECTOR        23
#define FLASH_MIN_ADDR          APPL_ADDRESS
#define FLASH_MAX_ADDR          0x08200000          // Last physical flash address
#define FLASH_BLOCK_SIZE        (128*1024)          // Size of one physical block from the flash
#define FLASH_SIZE              (FLASH_MAX_ADDR - FLASH_MIN_ADDR - FLASH_BLOCK_SIZE - sizeof(FlashInfoStruct))
#define FLASH_INFO_ADDRESS      (FLASH_MIN_ADDR + FLASH_SIZE)
#define RAM_MIN_ADDRESS         (0x20000000)
#define RAM_SIZE                (196603)
#define RAM_MAX_ADDRESS         (RAM_MIN_ADDRESS + RAM_SIZE)

/* End of Bootloader related definitions */

/* EPS related definitions */
#define BATT_LOW_3_5V                   1489
#define BATT_LOW_3_6V                   1531
#define BATT_LOW_3_7V                   1574
#define BATT_LOW_3_75V                  ((BATT_LOW_3_7V+BATT_LOW_3_8V)/2)
#define BATT_LOW_3_8V                   1617
#define BATT_LOW_3_85V                  ((BATT_LOW_3_8V+BATT_LOW_3_9V)/2)
#define BATT_LOW_3_9V                   1659
#define BATT_LOW_4_0V                   1702
#define BATT_LOW_4_1V                   1744

#define BATT_CURRENT_250mA              83
#define BATT_CURRENT_500mA              167
#define BATT_CURRENT_1000mA             333
/* End of EPS related definitions */

/* Gyroscope related definitions */
#define POWER_ON_GYRO_1  { HAL_GPIO_WritePin(GPIOB, PAN1_VGY_Pin, GPIO_PIN_RESET);  }
#define POWER_ON_GYRO_2  { HAL_GPIO_WritePin(GPIOB, PAN2_VGY_Pin, GPIO_PIN_RESET);  }
#define POWER_ON_GYRO_3  { HAL_GPIO_WritePin(GPIOB, PAN3_VGY_Pin, GPIO_PIN_RESET);  }
#define POWER_ON_GYRO_4  {  HAL_GPIO_WritePin(PAN4_VGY_GPIO_Port, PAN4_VGY_Pin, GPIO_PIN_RESET);  }
#define POWER_ON_GYRO_5  {  HAL_GPIO_WritePin(GPIOB, PAN5_VGY_Pin, GPIO_PIN_RESET);  }
#define POWER_ON_GYRO_6  {  HAL_GPIO_WritePin(GPIOB, PAN6_VGY_Pin, GPIO_PIN_RESET);  }

#define POWER_OFF_GYRO_1  { HAL_GPIO_WritePin(GPIOB, PAN1_VGY_Pin, GPIO_PIN_SET);  }
#define POWER_OFF_GYRO_2  { HAL_GPIO_WritePin(GPIOB, PAN2_VGY_Pin, GPIO_PIN_SET);  }
#define POWER_OFF_GYRO_3  { HAL_GPIO_WritePin(GPIOB, PAN3_VGY_Pin, GPIO_PIN_SET);  }
#define POWER_OFF_GYRO_4  {  HAL_GPIO_WritePin(PAN4_VGY_GPIO_Port, PAN4_VGY_Pin, GPIO_PIN_SET);  }
#define POWER_OFF_GYRO_5  {  HAL_GPIO_WritePin(GPIOB, PAN5_VGY_Pin, GPIO_PIN_SET);  }
#define POWER_OFF_GYRO_6  {  HAL_GPIO_WritePin(GPIOB, PAN6_VGY_Pin, GPIO_PIN_SET);  }
/* End of Gyroscope related definitions */

/* Accelerometer related definitions */
#define POWER_ON_ACC_1  { HAL_GPIO_WritePin(GPIOH, ACC1_EN_Pin, GPIO_PIN_RESET);  }
#define POWER_OFF_ACC_1  { HAL_GPIO_WritePin(GPIOH, ACC1_EN_Pin, GPIO_PIN_SET);  }
#define POWER_ON_ACC_2  { HAL_GPIO_WritePin(GPIOH, ACC2_EN_Pin, GPIO_PIN_RESET);  }
#define POWER_OFF_ACC_2  { HAL_GPIO_WritePin(GPIOH, ACC2_EN_Pin, GPIO_PIN_SET);  }
/* End of Accelerometer related definitions */

/* UHF related definitions */
  // Turn ON UHF
#define POWER_ON_UHF_1  { HAL_GPIO_WritePin(OBC_OUT5_GPIO_Port, OBC_OUT5_Pin, GPIO_PIN_SET); }
#define POWER_ON_UHF_2  { HAL_GPIO_WritePin(OBC_OUT6_GPIO_Port, OBC_OUT6_Pin, GPIO_PIN_RESET); }

  // Turn OFF UHF
#define POWER_OFF_UHF_1  { HAL_GPIO_WritePin(OBC_OUT5_GPIO_Port, OBC_OUT5_Pin, GPIO_PIN_RESET); }
#define POWER_OFF_UHF_2  { HAL_GPIO_WritePin(OBC_OUT6_GPIO_Port, OBC_OUT6_Pin, GPIO_PIN_SET); }
/* End of UHF related definitions */

#define	__disable_interrupt()	__disable_irq()
#define	__enable_interrupt()	__enable_irq()

#define SERVICE_TASK_PERIOD    (1000)
/*
*~~~~~~~~~~~~~~~~~~~~~~~~~~~~~~~~~~~~~~~~~~~~~~~~~~~~~~~~~~~~~~~~~~~~~~~~~~~~~~~~~~~~~~~~~~~
* EXTERNAL TYPES DECLARATIONS
*~~~~~~~~~~~~~~~~~~~~~~~~~~~~~~~~~~~~~~~~~~~~~~~~~~~~~~~~~~~~~~~~~~~~~~~~~~~~~~~~~~~~~~~~~~~
*/
/* No external types declared */

/*
*~~~~~~~~~~~~~~~~~~~~~~~~~~~~~~~~~~~~~~~~~~~~~~~~~~~~~~~~~~~~~~~~~~~~~~~~~~~~~~~~~~~~~~~~~~~
* EXTERNAL VARIABLES DECLARATIONS
*~~~~~~~~~~~~~~~~~~~~~~~~~~~~~~~~~~~~~~~~~~~~~~~~~~~~~~~~~~~~~~~~~~~~~~~~~~~~~~~~~~~~~~~~~~~
*/
extern FILE *COMM;
extern FILE *SYSCON;
extern FILE *PAYLOAD;
extern FILE *COM_SBAND;

extern uint32_t calendar_format;

/*
*~~~~~~~~~~~~~~~~~~~~~~~~~~~~~~~~~~~~~~~~~~~~~~~~~~~~~~~~~~~~~~~~~~~~~~~~~~~~~~~~~~~~~~~~~~~
* EXTERNAL ROUTINES DECLARATIONS 
*~~~~~~~~~~~~~~~~~~~~~~~~~~~~~~~~~~~~~~~~~~~~~~~~~~~~~~~~~~~~~~~~~~~~~~~~~~~~~~~~~~~~~~~~~~~
*/
void Error_Handler(void);

#endif    /* MAIN_H */
/* ~~~~~~~~~~~~~~~~~~~~~~~~~~~~~~~~~~~~~~~~~~~~~~~~~~~~~~~~~~~~~~~~~~~~~~~~~~~~~~~~~~~~~~~~~~~ */

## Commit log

2022-02-14 Doing some reorganization
    [CRD.brd, CRD.sch, SiPM.brd, SiPM.sch]
2022-09-25 Updated repo with all PCB versions
    [CRD.brd, CRD.sch, tiny.brd, tiny.sch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]

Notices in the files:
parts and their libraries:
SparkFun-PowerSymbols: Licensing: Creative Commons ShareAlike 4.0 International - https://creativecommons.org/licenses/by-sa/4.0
